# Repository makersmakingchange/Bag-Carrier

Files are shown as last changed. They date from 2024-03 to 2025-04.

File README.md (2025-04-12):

# Bag Carrier

## Overview

The bag carrier is a low-cost, 3D-printed handheld tool that distributes the weight of bags carried. This 3D Printed Assistive Device can assist people with arthritis or other disabilities to carry plastic bags and reusable bags. The bag handles can easily loop around the two curved hooks. The handle is rounded to allows users to comfortably grip the carrier.

[Makers Making Change Assistive Device Library Listing](https://www.makersmakingchange.com/s/product/bag-carrier/01tJR00000068yzYAA)

Last Updated: 2023-Mar-27

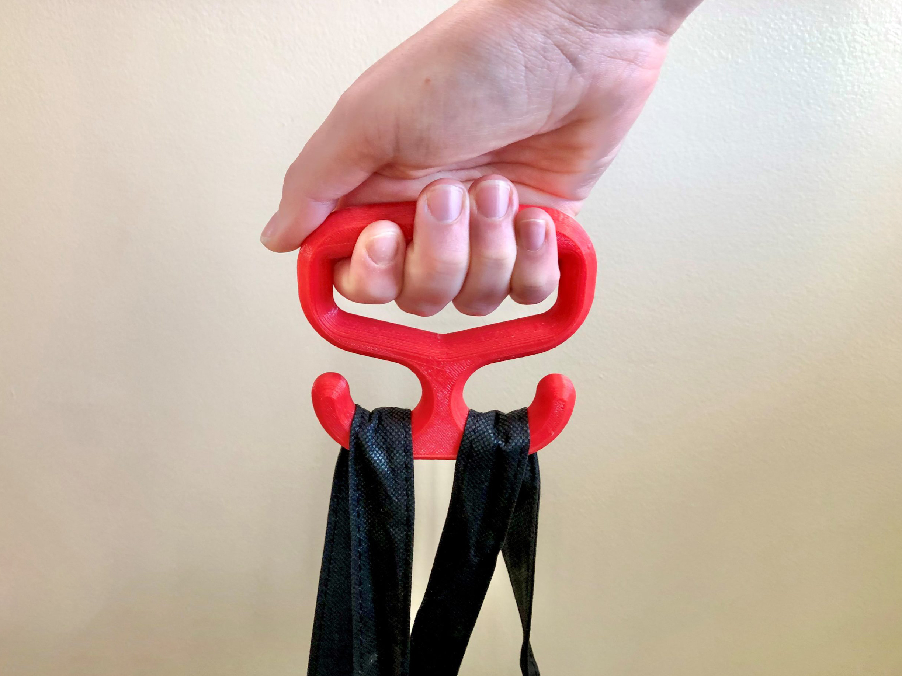
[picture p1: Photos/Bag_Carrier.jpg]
Picture of person using a red 3d printed Bag Carrier to lift some black reusable grocery bags.


## Usage

This handle is used to assist in carrying plastic or reusable bags by offering a wider grip and more distributed loading. This handle can either be carried in hand or can be attached onto the side of a wheelchair. See the [User Guide](/Documentation/Bag_Carrier_User_Guide.pdf) for additional information.

## Build Instructions

All documentation, design files, and photos are contained within this repository. The [Maker Checklist]([/Documentation/Bag_Carrier_Maker_Checklist.pdf)) found in Documents will aid you in following the correct steps to build it yourself or work with a requester. 

### SKILLS REQUIRED
3D Printing

### TOOLS

3D Printer

### 3D PRINTING

The design is intended to print in PLA with no supports. 3D print STL's and instructions can be found on the GitHub page linked at the top of this project page.

## Sizing

There are small, medium, and large handles available for different sized hands. A printable [sizing guide](/Documentation/Bag_Carrier_Sizing_Guide.pdf) can be used to find the correct sizing for a user.

## Attribution
An original Bag Carrier was designed by Neil Squire Society / Makers Making Change. This is an updated, redsigned version of the original design.

### Contributors
 - Kerilyn Kennedy - Neil Squire Society / Makers Making Change
 - Jake McIvor - Neil Squire Society / Makers Making Change

---
<!-- ABOUT MMC START -->
## About Makers Making Change
[Makers Making Change Logo](https://www.makersmakingchange.com/)

Makers Making Change is a program of [Neil Squire](https://www.neilsquire.ca/), a Canadian non-profit that uses technology, knowledge, and passion to empower people with disabilities.

Makers Making Change leverages the capacity of community based Makers, Disability Professionals and Volunteers to develop and deliver affordable Open Source Assistive Technologies.

 - Website: [www.MakersMakingChange.com](https://www.makersmakingchange.com/)
 - GitHub: [makersmakingchange](https://github.com/makersmakingchange)
 - Bluesky: [@makersmakingchange.bsky.social](https://bsky.app/profile/makersmakingchange.bsky.social)
 - Instagram: [@makersmakingchange](https://www.instagram.com/makersmakingchange)
 - Facebook: [makersmakechange](https://www.facebook.com/makersmakechange)
 - LinkedIn: [Neil Squire Society](https://www.linkedin.com/company/neil-squire-society/)
 - Thingiverse: [makersmakingchange](https://www.thingiverse.com/makersmakingchange/about)
 - Printables: [MakersMakingChange](https://www.printables.com/@MakersMakingChange)

### Contact Us
For technical questions, to get involved, or to share your experience we encourage you to [visit our website](https://www.makersmakingchange.com/) or [contact us](https://www.makersmakingchange.com/s/contact).
<!-- ABOUT MMC END -->

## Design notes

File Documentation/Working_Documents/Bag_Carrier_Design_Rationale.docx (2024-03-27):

# Introduction

The bag carrier is a low-cost, 3D-printed handheld tool that distributes the weight of bags carried. This 3D Printed Assistive Device can assist people with arthritis or other disabilities to carry plastic bags and reusable bags. The bag handles can easily loop around the two curved hooks. The handle is rounded to allows users to comfortably grip the carrier.

# Research

In order to determine how strong the bag carrier must be, it was required to determine how much weight someone can comfortably carry with one arm. It was found that 25lbs could be considered on the heavy end of what someone might carry in their grocery bags with one arm.

In order to design different sized handles, glove sizing charts were researched to help determine appropriate sizing.

# Requirements

There was a pre-existing bag carrier on the MMC site. It was found that this handle had too long of a print time and was quite bulky. With those in mind, the key requirements for the new design were:

- That it is strong enough to carry groceries
- Decrease the print time

# Ideation

It was thought to design a handle with 2 handles in somewhat of a T formation in order to increase the strength vs size of the handle. It was also thought to have 3 different sizes to better accommodate different sized hands.

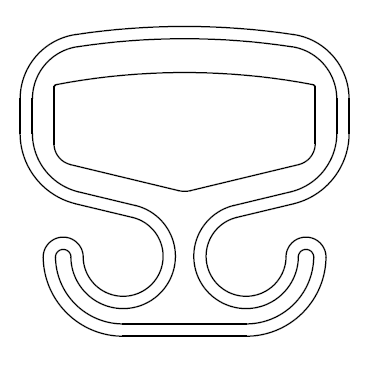
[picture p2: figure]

# Prototyping

Several prototypes were made during the duration of this project. Factors that changed between prototypes included: height and width of handle hole, handle thickness, hook size, and how rounded the handle was. The width of the handle holes was determined by using a glove sizing chart to determine a suitable small medium, and large sized handle. The height of the handle hole increases for the larger sizes. The handle was rounded after initial prototypes had rougher edges that were undesirable if the user used the bag carrier for an extended period of time. The hook size was optimized through strength testing.

# Testing

Strength testing was conducted on the handles to ensure that the handles were strong enough to carry a load of groceries. A safety factor of 2 was applied during the testing period, testing up to 50lbs on the handles which is way above what the average person would comfortably. Testing allowed for the size of the hooks to be optimized – making the hooks smaller allowed the print time of the bag carrier to stay low. Handles were tested in one-minute intervals holding 20, 30, 40 and then 50lbs. It was considered a successful design when it was able to hold 50lbs for 1 minute without breaking.

# Final Design

Found below is a picture of the 3 different sized handles, large (left), medium (middle), and small (right). Each handle has the same size hooks and can hold approximately the same weights.

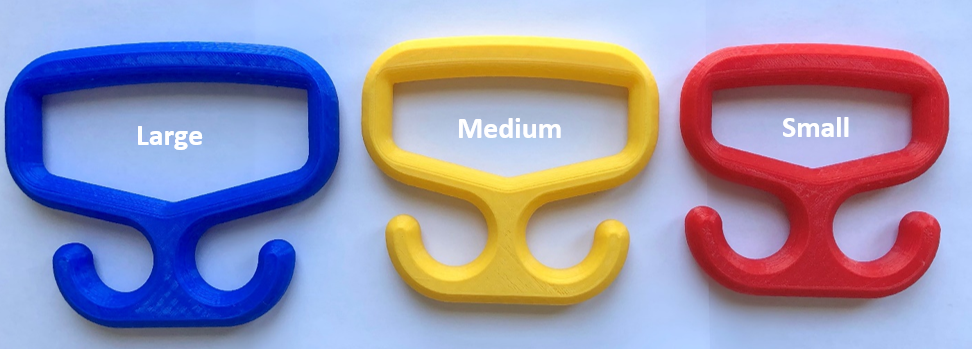
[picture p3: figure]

© 2021 by <Author>. This work is licensed under the CC BY SA 4.0 License: http://creativecommons.org/licenses/by-sa/4.0 Files available at <Replace with MMC Library Link> Page 1 of 1

V2.0 | FEB 2022 Bag Carrier Design Rationale

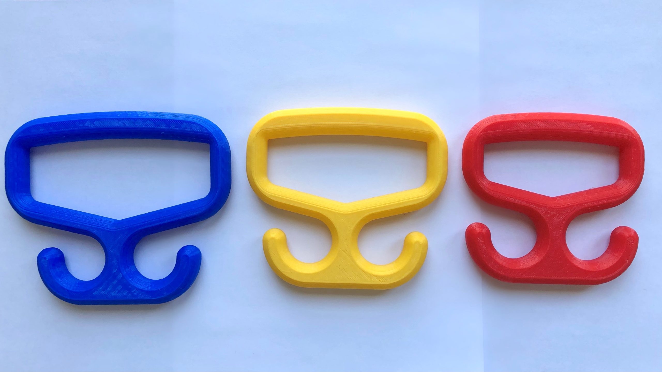
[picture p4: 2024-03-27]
Photos/3-bag-handles.jpg

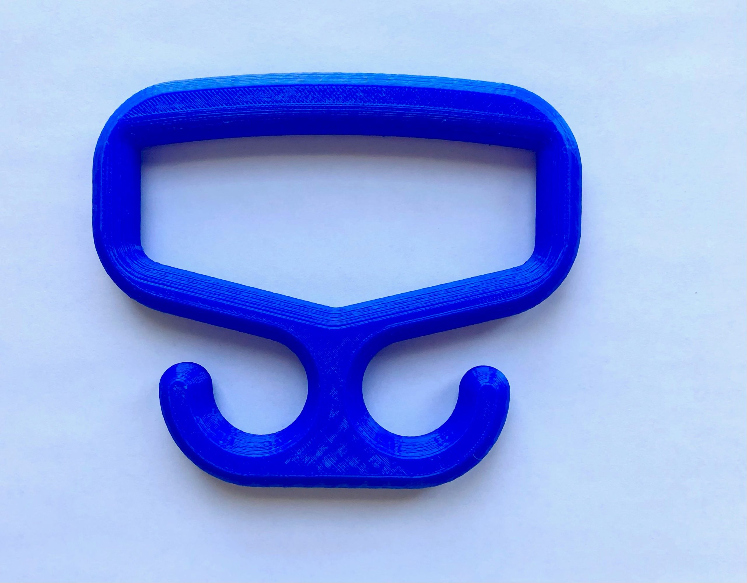
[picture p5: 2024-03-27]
Photos/bag-handle-large.jpg

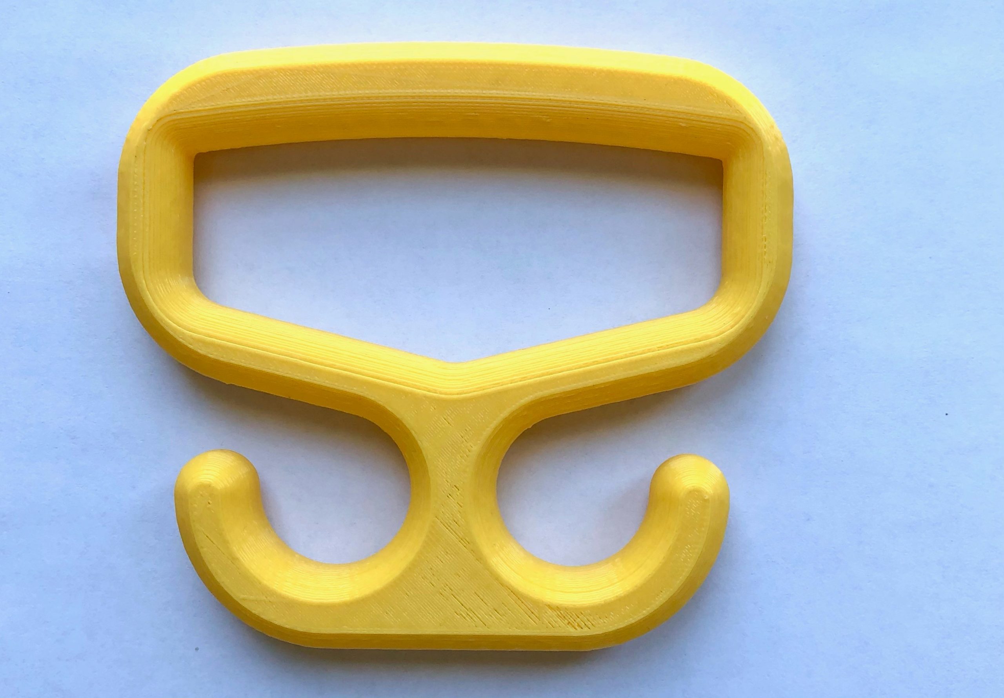
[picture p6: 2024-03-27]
Photos/bag-handle-medium.jpg

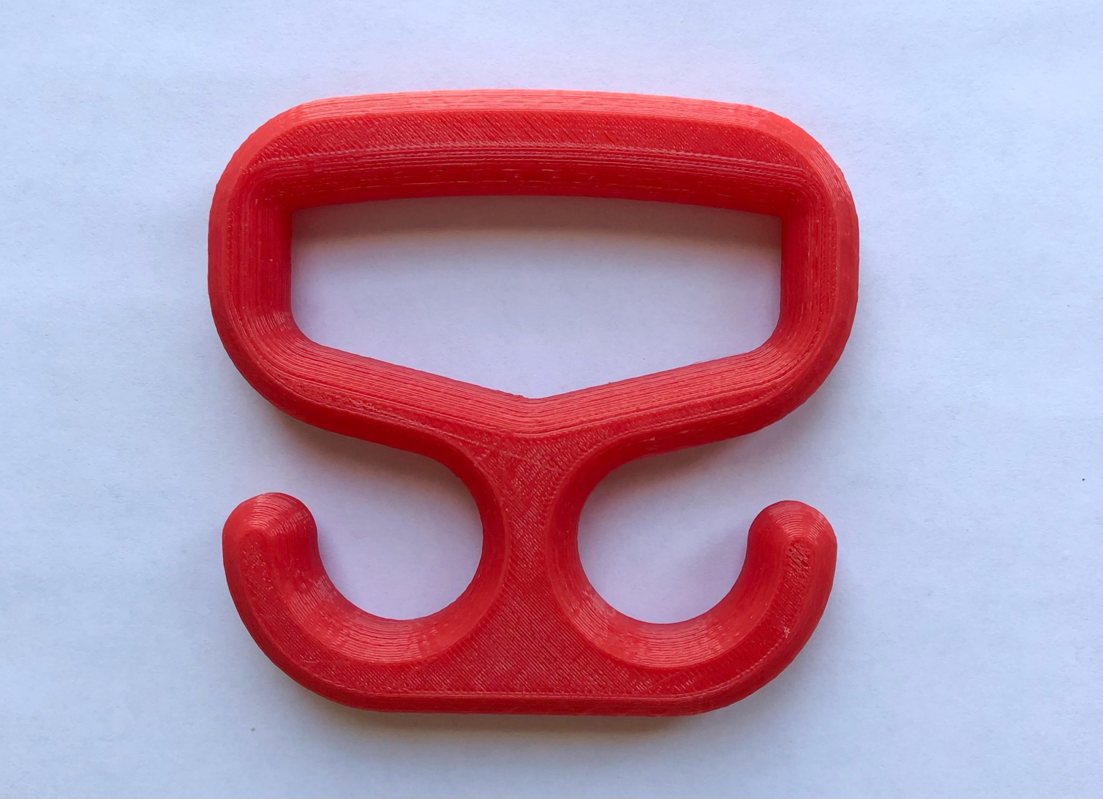
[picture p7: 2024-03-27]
Photos/bag-handle-small.jpg

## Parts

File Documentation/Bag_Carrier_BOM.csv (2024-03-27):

Bag Carrier |  | Total Cost | Total Print time (hr) | Total filament (g)
Version: V2.0.1 | Last updated: 2024-Mar-27 | #DIV/0! | 2.23 | 41
Commercial Parts:
 | Part Name | Quantity Needed | Pkg Quantity | Price per package | Price per Unit | Price for qty needed | Link
<None> |  |  |  |  | #DIV/0! | #DIV/0!
 |  |  |  |  | #DIV/0! | #DIV/0!
 |  |  |  |  | #DIV/0! | #DIV/0!
3D Printed Parts ESTIMATED PRICING USING 1KG ROLL COST: | $25.00
Part | Description | Quantity Needed | TOTAL Mass (g) | Estimated Price | Print Time (Min) | Link
Large Bag Carrier - small and medium will cost slightly less |  | 1 | 41 | $1.03 | 134
 |  |  |  | $-
 |  |  |  | $-
 |  |  |  | $-
 |  |  |  | $-
 |  |  | Total Print Cost: | $1.03
Tools for Assembly
<None>
s
Alternatives (if there are other sources for some parts link them below)
Part and description | Link

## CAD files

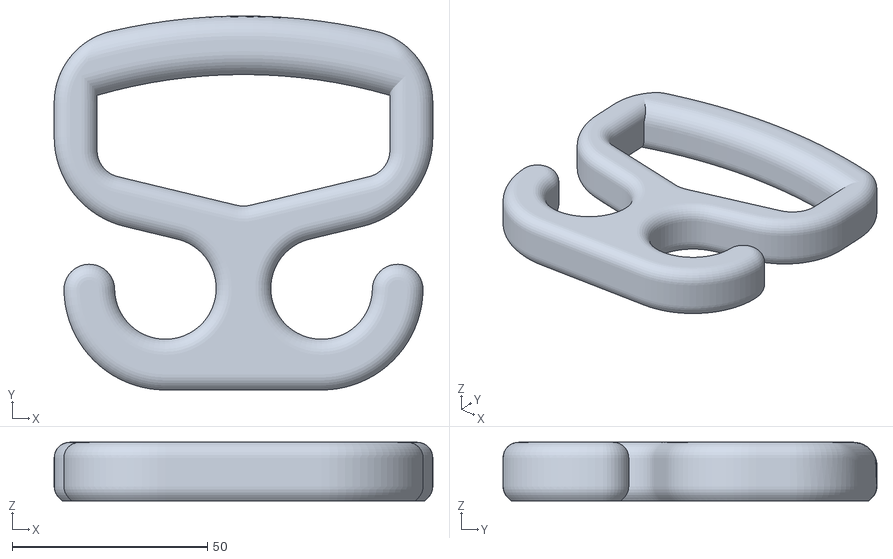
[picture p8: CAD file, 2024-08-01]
Build_Files/3D_Printing_Files/Bag_Carrier_Small.stl
97.0 x 95.8 x 15.0

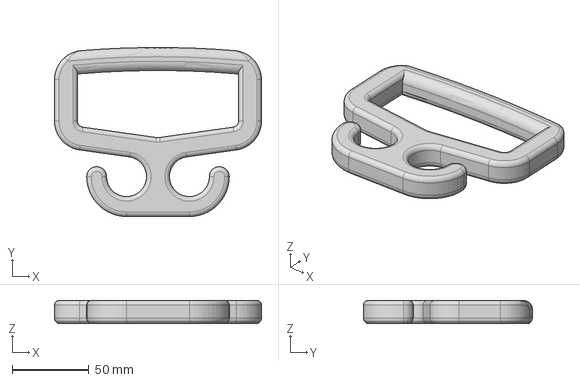
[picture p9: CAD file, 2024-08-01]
Design_Files/Bag_Carrier_Large_One_Piece v2.step
135.0 x 110.2 x 15.0 mm

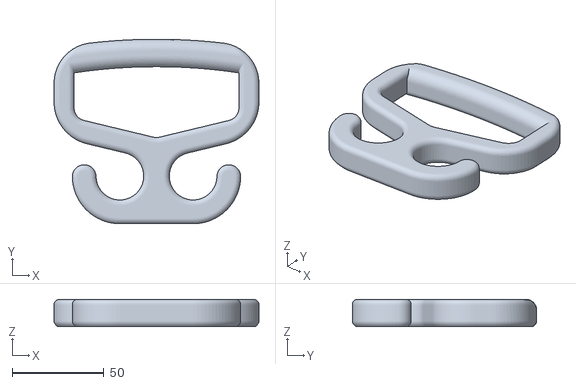
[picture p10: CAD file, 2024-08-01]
Build_Files/3D_Printing_Files/Bag_Carrier_Medium.stl
112.0 x 100.8 x 15.0

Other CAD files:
Build_Files/3D_Printing_Files/Bag_Carrier_Large.stl
Design_Files/Bag_Carrier_Small_One_Piece v1.step
Design_Files/Bag_Carrier_Medium_One_Piece v5.step
Design_Files/Bag_Carrier_Large_One_Piece v2.f3d
Design_Files/Bag_Carrier_Medium_One_Piece v5.f3d
Design_Files/Bag_Carrier_Small_One_Piece v1.f3d

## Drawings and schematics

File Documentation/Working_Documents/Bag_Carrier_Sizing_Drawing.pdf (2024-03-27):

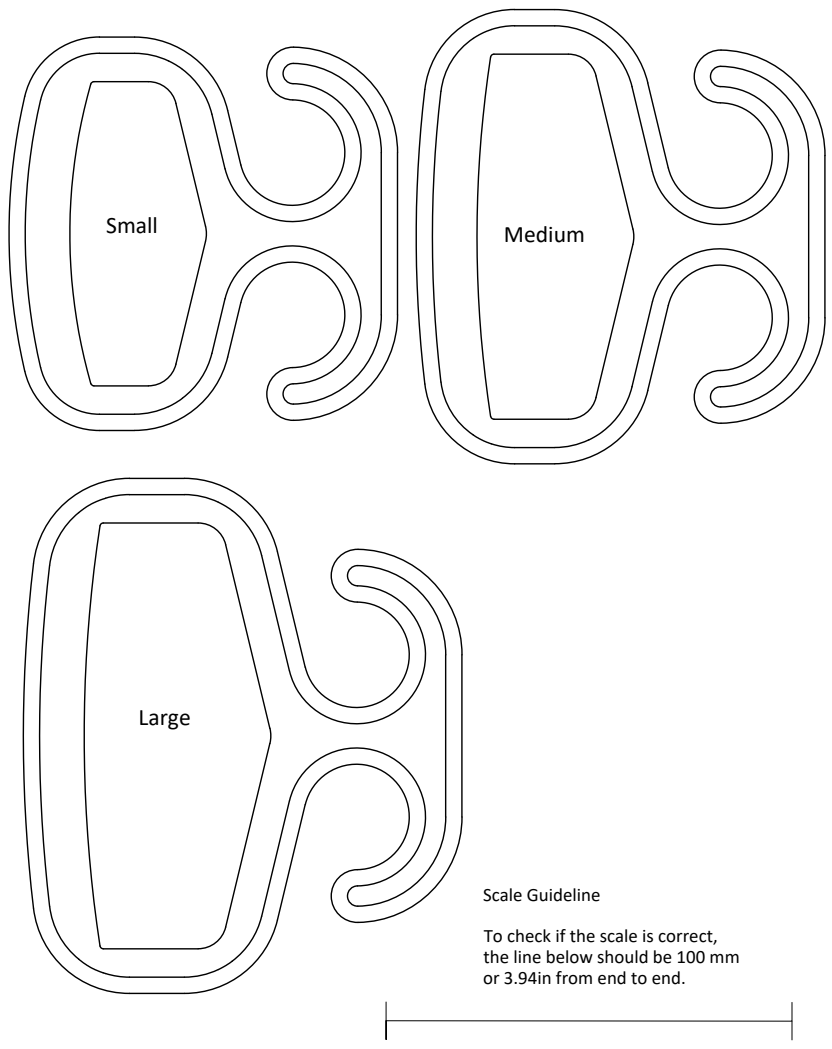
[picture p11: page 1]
Scale Guideline

To check if the scale is correct,
the line below should be 100 mm
or 3.94in from end to end.

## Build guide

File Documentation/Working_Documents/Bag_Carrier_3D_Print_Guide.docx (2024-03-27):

# 3D Printing Summary

Metrics | Small | Medium | Large
Total Print Time (min) | 112 | 123 | 134
Total Number of Components | 1 | 1 | 1
Typical Total Mass (g) | 35 | 38 | 41
Typical Number of Print Setups | 1 | 1 | 1

# 3D Printing Settings

Print File Name | Qty | Total Print Time (hr:min) | Mass (g) | Infill (%) | Support (Y/N) | Layer Height/ Nozzle Diameter (mm) | Notes (orientation, special settings, etc)
Bag_Carrier_Small.stl | 1 | 1:52 | 35 | 20 | N | 0.3/0.4 | Print in orientation given in STL
Bag_Carrier_Medium.stl | 1 | 2:03 | 38 | 20 | N | 0.3/0.4 | Print in orientation given in STL
Bag_Carrier_Large.stl | 1 | 2:14 | 41 | 20 | N | 0.3/0.4 | Print in orientation given in STL

# Post-Processing

These handles are printed without supports; hence no post-processing is required.

# Customization Options

The user can request that the device be printed in multiple colours.

# Examples of Quality Prints

Below is a picture of what print quality is expected from printing this device.


© 2021 by <Author>. This work is licensed under the CC BY SA 4.0 License: http://creativecommons.org/licenses/by-sa/4.0 Files available at <Replace with MMC Library Link> Page 1 of 2

V2.0 | FEB 2022 Bag Carrier 3D Printing Guide

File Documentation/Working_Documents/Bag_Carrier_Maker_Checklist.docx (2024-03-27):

# Maker To Do List

Ask the requester to print off the User Quick Guide so they can determine which size bag carrier would best fit them.

- Determine the cost of materials and relay this cost to the user before printing to ensure the requester is comfortable with the price.
- Ask the requester if they want any customizations to the device (e.g., color).
- Print the device.
- Deliver the device and User Quick Guide to the requestor.

# Items to Give to User

- User Quick Guide
- Bag Carrier

© 2021 by <Author>. This work is licensed under the CC BY SA 4.0 License: http://creativecommons.org/licenses/by-sa/4.0 Files available at <Replace with MMC Library Link> Page 1 of 1

V2.0 FEB 2022 Bag Carrier Maker Checklist

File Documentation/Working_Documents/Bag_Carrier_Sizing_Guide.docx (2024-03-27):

## Introduction

The Bag Carrier is a low-cost, 3D-printed handheld tool that distributes the weight of bags carried. This 3D Printed Assistive Device can assist people with arthritis or other disabilities to carry plastic bags and reusable bags. The Bag Carrier comes in 3 different sizes: small, medium, and large.

## Sizing

| Weight (g) | Dimensions (mm)
| | Width | Height | Grip Width | Thickness
Small | 35 | 97 | 96 | 75 | 46
Medium | 38 | 113 | 101 | 90 | 46
Large | 41 | 127 | 106 | 105 | 46

## Sizing Instructions

1. Print out the next page. It should be set to letter sized paper with no scaling.
2. With a ruler, measure the scale guideline to ensure that it was printed to scale.
3. Extend your hand out with your fingers together. Align the bottom section of your pointer finger with the line of the left of the hole of the handle. If your four fingers fit between the 2 lines, the handle should be large enough.
4. Select the appropriate size.

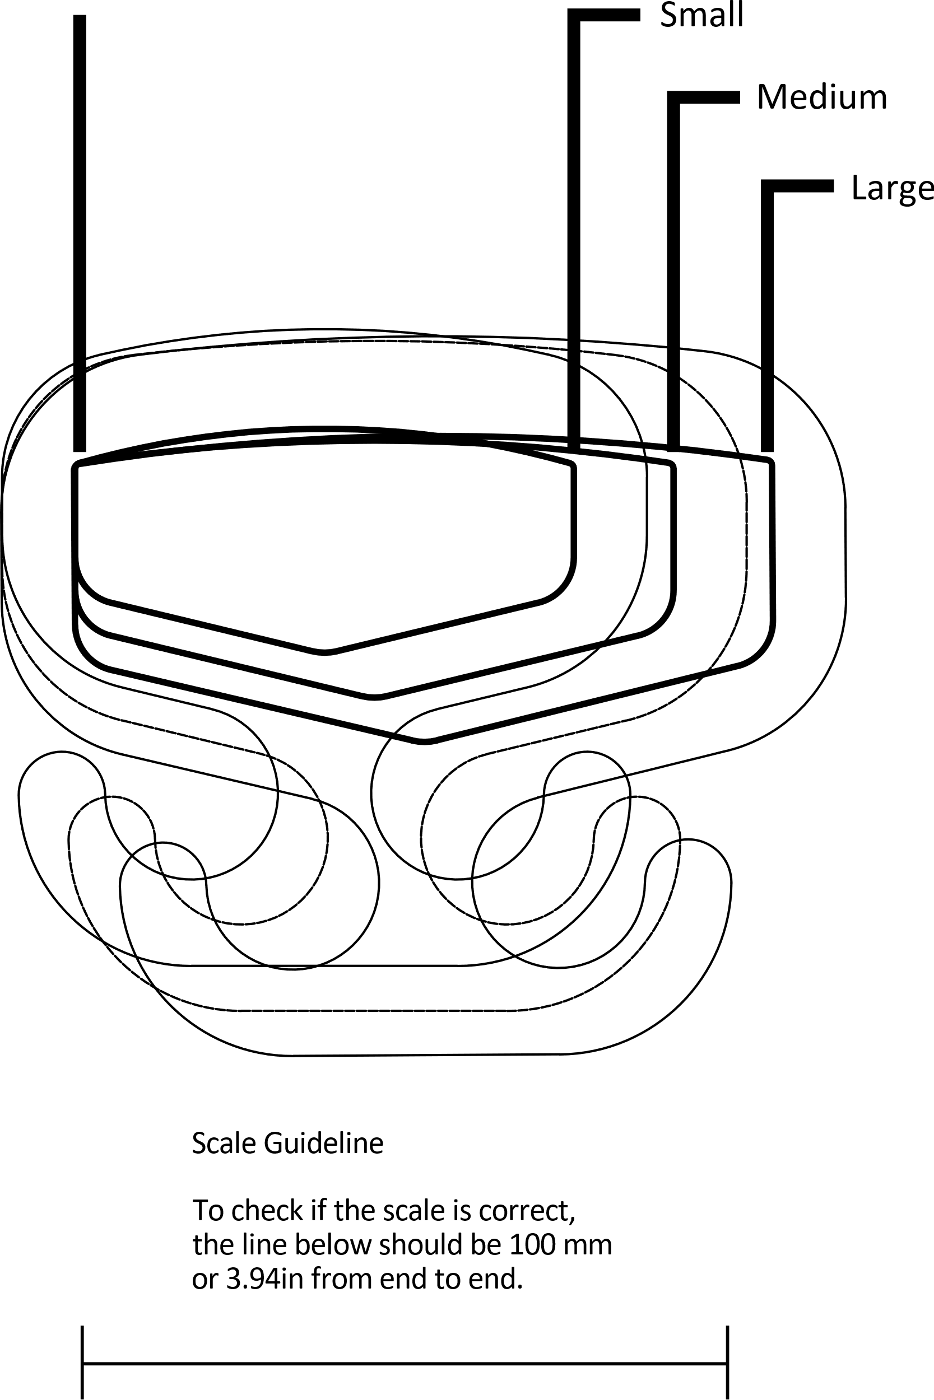
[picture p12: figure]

© 2021-2024 by Neil Squire Society. This work is licensed under the CC BY SA 4.0 License: http://creativecommons.org/licenses/by-sa/4.0 Files available at https://github.com/makersmakingchange Page 1 of 1

V2.0.1 | MARCH 2024 Bag Carrier SIZING Guide

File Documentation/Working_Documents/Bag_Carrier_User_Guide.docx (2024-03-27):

## Introduction

The Bag Carrier is a low-cost, 3D-printed handheld tool that distributes the weight of bags carried. This 3D Printed Assistive Device can assist people with arthritis or other disabilities to carry plastic bags and reusable bags. The Bag Carrier comes in 3 different sizes: small, medium, and large.

## Features

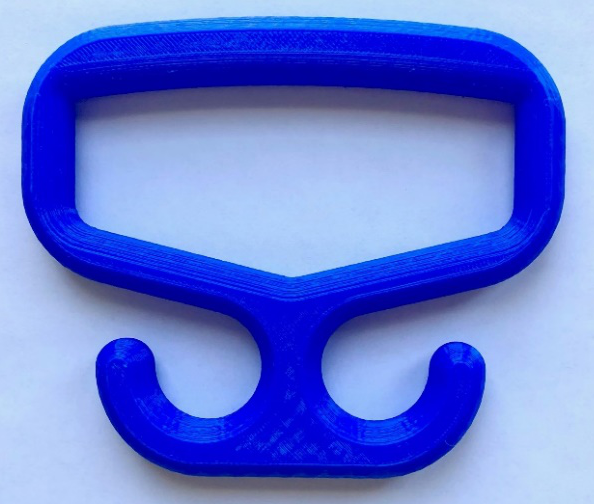
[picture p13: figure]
Labelled image of Bag Carrier with handle at the top and two curved bag hooks on the bottom.
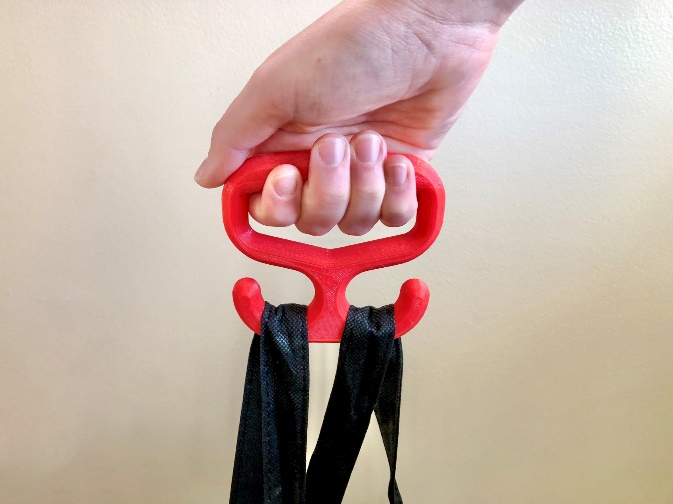
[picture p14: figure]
Picture of a hand holding bag carrier with bag attached to hooks.

Handle

Bag Hook

Bag Hook

## Usage

This handle is used to carry plastic or reusable bags. This handle can either be carried in hand or can attach onto the side of a wheelchair. The bag handles can easily loop around the two curved hooks.

## Compatibility

There are 3 different sized handles in order to try and accommodate many different hand sizes. Please refer to the Sizing Guide to determine which size handle will work best for you.

## Specifications

Version | Weight (g) | Dimensions (mm)
| | Overall Width | Overall Height | Grip Width | Thickness
Small | 35 | 97 | 96 | 75 | 46
Medium | 38 | 113 | 101 | 90 | 46
Large | 41 | 127 | 106 | 105 | 46

## Cleaning

The Bag Carrier can be cleaned with warm soapy water. Do not expose the device to high heat as it may deform or break. (i.e., do not put it in the dishwasher or washing machine).

© 2021-2024 by Neil Squire Society. This work is licensed under the CC BY SA 4.0 License: http://creativecommons.org/licenses/by-sa/4.0 Files available at https://github.com/makersmakingchange/Bag-Carrier Page 1 of 1

V2.0.1 | MARCH 2024 Bag Carrier user Guide

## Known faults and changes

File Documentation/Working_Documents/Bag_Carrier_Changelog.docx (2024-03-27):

# Version 2.0.1 | 2024-Mar-27

- Refactored User Guide with labelled diagram
- Separated out and updated sizing guide

# Version 2.0 | 2022-Feb-02

This is a newly designed handle to replace the old one.

Improvements:

- Significantly reduced print time
- Designed 3 different sized handles to better accommodate different sized hands. The width and the height of the handle hole increases for the larger sized handles.
- Made the handle less bulky.
- Increased the strength per gram of the handle by connecting the two hooks.


# Version 1.0 | 2018-Jan-01

This bag carrier was very strong, but ultimately replaced as the print time was much too long, and the handle was quite bulky.

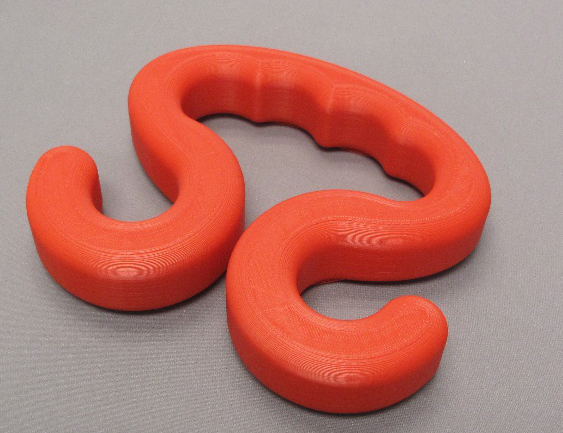
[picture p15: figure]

© 2021 by <Author>. This work is licensed under the CC BY SA 4.0 License: http://creativecommons.org/licenses/by-sa/4.0 Files available at <Replace with MMC Library Link> Page 1 of 1

V2.0 | FEB 2022 Bag Carrier changelog

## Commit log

2024-03-27 Reorganize 3D Printing Files
    [Bag_Carrier_Large.stl, Bag_Carrier_Medium.stl, Bag_Carrier_Small.stl]
2024-03-27 Organize design files
    [Bag Carrier.f3d, Bag Carrier.step]
2024-03-27 Add working documents
    [Bag_Carrier_BOM.xlsx]
2024-03-27 Update BOM
    clean up
    [Bag_Carrier_BOM.xlsx]
2024-03-27 Add device photos
2024-03-27 Create CSV as BOM
    [Bag_Carrier_BOM.csv, Bag_Carrier_BOM.xlsx]
2024-08-01 Updated print files
    Updated print files to improve bed adhesion and grip comfort
    [Bag Carrier.f3d, Bag Carrier.step, Bag_Carrier_Large.stl, Bag_Carrier_Large_One_Piece v2.f3d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]
